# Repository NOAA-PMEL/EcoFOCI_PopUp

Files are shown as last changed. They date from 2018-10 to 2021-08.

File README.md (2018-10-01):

# EcoFOCI_PopUp

Under Ice 'Pop-Up' Buoy

################

Legal Disclaimer

This repository is a software product and is not official communication of the National Oceanic and Atmospheric Administration (NOAA), or the United States Department of Commerce (DOC). All NOAA GitHub project code is provided on an 'as is' basis and the user assumes responsibility for its use. Any claims against the DOC or DOC bureaus stemming from the use of this GitHub project will be governed by all applicable Federal law. Any reference to specific commercial products, processes, or services by service mark, trademark, manufacturer, or otherwise, does not constitute or imply their endorsement, recommendation, or favoring by the DOC. The DOC seal and logo, or the seal and logo of a DOC bureau, shall not be used in any manner to imply endorsement of any commercial product or activity by the DOC or the United States Government.

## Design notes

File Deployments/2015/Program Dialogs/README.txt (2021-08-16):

The 2015 prototypes did not have an arduino program to print a dialog or sampling schedule
They were proof of concept floats that had a wildlife computer attached
No program dialogs applicable for the prototype floats in 2015.
(S. Donohoe, 10/27/2020)

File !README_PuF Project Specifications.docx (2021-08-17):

Pop-up Project Specifications

(Low Cost Expendable Buoys for Under Ice Data Collection, Innovative Technology for Arctic Exploration (ITAE))

October 10, 2019

National Oceanic and Atmospheric Administration (NOAA)

Pacific Marine Environmental Lab (PMEL)

Ecosystem Fisheries-Oceanography Coordinated Investigations (EcoFOCI)

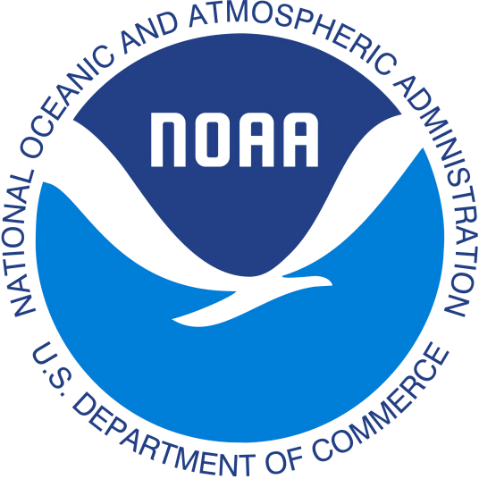
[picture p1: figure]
Image result for NOAA logo

# Revision History

The table below identifies all changes that have been incorporated into this document.

Version | Draft Date | Summary of Changes
1.0 | 10/10/2019 | Initial draft

# Table of Contents

Revision History 2

Table of Contents 3

INTRODUCTION 4

Purpose 4

Scope 4

IMMEDIATE SCIENCE APPLICATIONS 4

Under Ice Production 4

Measure conditions and productivity levels under sea ice. 4

Bering Cold Pool 4

Measure conditions in the Bering Sea to map the cold pool. 4

LONG-TERM PROJECT VISION 4

Measurements of Interest 5

Sampling Phases 6

ENGINEERING SPECIFICATIONS 6

Basic Program Flow 6

Mechanical Design Parameters 7

Sensor Capability/Data Quality 8

Battery Life/Data Quantity 10

APPENDIX A: ACRONYMS AND ABBREVIATIONS 10

APPENDIX B: CITATIONS 10

# INTRODUCTION

## Purpose

This document is to identify goals for the pop-up project that cover: overall project direction, specific engineering requirements, data quality and sensor capability requirements and cost requirements.

## Scope

This document is intended for use as a developmental tool while the pop-up project is under the auspices and funding of the ITAE program [1] (https://www.researchgate.net/publication/290392540_Innovative_technology_development_for_Arctic_Exploration). The pop-up project is a collaborative effort between EcoFOCI and the PMEL Engineering Development Division (EDD). Initial prototyping and development of the pop-up floats began under Lieutenant Daniel Langis, NOAA Corps in 2015 [2] (https://www.researchgate.net/publication/330300648_Low-Cost_Expendable_Buoys_for_Under_Ice_Data_Collection).

# IMMEDIATE SCIENCE APPLICATIONS

## Under Ice Production

### Measure conditions and productivity levels under sea ice.

  - The primary interest is in productivity at the water-ice boundary where productivity is very high in the spring before ice melt and ambient light levels are rapidly rising.

## Bering Cold Pool

### Measure conditions in the Bering Sea to map the cold pool.

  - Bottom temperatures below 2 °C characterize the Bering Sea cold pool, an important refuge for young pollock from predation. The primary interest is in measuring the extent, thickness and varying light levels of the cold pool through the winter months and how it changes over time.

# LONG-TERM PROJECT VISION

“Robust, inexpensive, and expendable, but sophisticated enough to acquire oceanographic-quality data.”

The pop-up float was developed as a unique product designed to fill the gap in available technology between year-round deeper moorings and surface-based sampling in the summers. However, because of the harsh and unpredictable environment of shifting and breaking ice, actually acquiring measurements close to the ice during the winter and spring without losing instruments has been notoriously difficult. The pop-up project aims to develop a low-cost, expendable oceanographic instrument that can be easily deployed by hand from any vessel and that will reliably transmit data back via satellite.

Long-term goals for this project include:

- maintaining low-cost production and deployment (~$3,000 / pop-up)
- an environmentally friendly design with biodegradable materials (glass, cork, metals)
- up to 24 month at-sea endurance
- the ability to send commands with 2-way communication to the float (commands to resend data files, change sampling frequencies...etc.)
- a modular design that allows sensors to be added or removed easily depending on mission and budget requirements.

## Measurements of Interest

Measurements of interest vary for the two current science applications: Bering Cold Pool and Under Ice Production. The Bering Cold Pool application focuses on temperature measurements with highest interest in further development to include a dissolved oxygen sensor. The Under Ice Production application focuses on Fluorescence and PAR, with interest in improving current camera capabilities.The following bulleted lists for each science application show the core instrument package for all floats in blue and additional sensors in order of priority.

    - GPS (only used during surface drifter mode)
    - Iridium SBD (only used during surface drifter mode)
    - Clock / Timer (RTC)
    - Profile (Primary) Temperature Probe (PTP)
    - Sea Surface (Secondary) Temperature (SST)
    - Pressure Sensor
    - Tilt
    - Fluorometer
    - Photosynthetically active radiation (PAR) (light months only)
    - Camera
    - Oxygen [currently cost-prohibitive]
    - Salinity [currently cost-prohibitive]

## Sampling Phases

The pop-up has a 5 phase sampling program: Anchored, Profile, Under Ice, Transmit and Surface Drifter. Each of these phases is run sequentially. Prior to the programmed unit start date, the pop-up is in sleep mode and is not sampling any sensors. The pop-up’s real time clock (RTC) functions as an alarm, which will wake up the unit and initiate the first sampling phase (Anchored) at the unit start date/time.

--ANCHORED--

This mode starts at the scheduled Start Time.

Unit will start sampling [Oct 01 2019 00:00:00] and take a sample every (1h,0m,0s)

--PROFILE--

This mode starts just before the scheduled Release Time.

Release Expected [Jun 01 2020 00:00:00] (<--Set Burn Wire Release for this exact time/date.)

Unit will wake up (2h,0m,0s) before scheduled release and wait for profile.

Start of profile will be triggered by a change in depth of (1 meters).

Profile will sample at 4 Hz for (0h,1m,30s) seconds before proceeding to phase 3.

If unit does not sense the release within (4h,0m,0s) of waking it will assume it missed the profile and proceed to the UNDER ICE phase.

--UNDER ICE --

This mode starts after profile has been collected (or missed).

Unit will take a sample every (1h,0m,0s) and take an image once a day.

Unit will search for GPS satellites for (0h,2m,0s) after every sample.

When unit acquires GPS fix, it will proceed to the TRANSMIT phase.

--TRANSMIT--

If unit does successfully find a GPS satellite, it will attempt to send all collected data back in the following order:

1-File Summary, 2-Profile Data, 3-Under Ice Data, 4-Bottom Data, 5-Daily Images

If any iridium messages send successfully, it will continue sending until one message fails and make the next attempt to send in (0h,20m,0s)

Otherwise, if no messages sent, the unit will take the next sample and attempt to send again in (1h,0m,0s)

--SURFACE DRIFTER--

This mode starts after all data has finished sending.

Unit will take a sample every (3h,0m,0s) and search for a GPS fix for (0h,2m,0s) after every sample.

Unit will attempt to send any new data regardless of whether a GPS fix was found

# ENGINEERING SPECIFICATIONS

## Basic Program Flow

A. Wake Up

B. Determine phase based on current date/time and programmed cutoff dates/times

0 = Initial programming (before start date)

If mode = 0, display parameters and shut down after user removes USB, don’t take any sample data

1 = Anchored

2 = Wait for Profile

3 = Under Ice

4 = Surface Drifter

C. Determine next sample time/date and set RTC alarm

D. Collect Sensor Data, Store to SD Card

E. If phase = 1 (Anchored)

Do nothing else, just go to sleep

F. If phase = 2 (Profile)

Take initial depth measurement

Continuously take depth readings and compare to initial measurement

Wait for depth to change by m meters

Start profile

Collect profile data at 4 Hz for p seconds

Go to sleep

G. If phase = 3 (Under Ice)

**This mode is used primarily to preserve battery power. In this mode the unit will only attempt to search for GPS once a day, rather than every hour.**

If hour = 23 UTC (1500 AKST, close to solar noon in most of Alaska)

Search for GPS for g seconds, n times, with delay in between

If GPS lock is found n times

Store GPS location and time on SD Card

Attempt to transmit iridium data

Else

Do nothing else, just go to sleep

H. If phase =4 (Surface Drifter)

Search for GPS for g seconds, n times, with delay in between

If GPS lock is found n times store GPS location and time on SD Card

Attempt to transmit iridium data

Else

Do nothing else, just go to sleep

## Mechanical Design Parameters

Trawl Housing Depth Rating: 200m, tested to max of 940psi (652m) at which point acrylic

camera housing cracked. Trawl float and delrin sensor housings withstood 940psi.

Buoyancy & GM:

The 12” trawl float provided ~28lb(?) net buoyancy. The net buoyancy should be tailored to produce the desired profile speed, while also providing adequate freeboard.

Profile speed: desired: ???? / actual: 1m/s

Freeboard: Generation 2 - 2.5” of freeboard

Generation 3 - 3.5” of freeboard

Generation 3.1 - 2.5” of freeboard

Total Dry Weight: Generation 2 - 13,305 g

Generation 3 - 11,263 g

Generation 3.1 - 13,305 g

Anchor Weight:

50lb Chain Link, 1m cable length

The anchor weight should be sufficient to keep the float from moving in high currents.

## Sensor Capability/Data Quality

Topside Temperature Probe (TTP) [Primary]*[3-4m resolution, ±0.01°C @4Hz]

Sensor: TTI inc, USP19572 REVA

Absolute Accuracy: ±0.01°C or better

Range: -5°C to +70°C

Resolution: 0.0006°C @ -2°C

0.001°C @ 10°C

0.002°C @25°C

0.01°C @50°C

Sea Surface Temperature (SST) [Secondary]*[3-4m resolution, ±0.01°C @4Hz]

Sensor: In-House (NTC Thermistor 50k Bead Epoxy,

Hex Head Plug 1/16”, Arctic Silver Alumina)

Absolute Accuracy: ±0.01°C or better

Range: -5°C to +70°C

Pressure Sensor *[ 3-4m resolution, ±1m @4Hz ]

Sensors: Keller PA-4LD OEM Pressure Transmitter (http://www.keller-druck.com/picts/pdf/engl/4ld_9ld_e.pdf)

Absolute Accuracy: ±70cm (10 bar) / ±0.7%FS

Range: 0 to 100m (10 bar) / 0 to 300m (30bar)

Resolution: 0.3cm (10 bar) /

GPS *[Position Accuracy ~3meters 50% CEP]

Unit: AMC-PA6H Alphamicro (http://www.alphamicrowireless.com/franchises/globaltop-technology/pa6h.aspx)

High Sensitivity: -165 dBm, TCXO Design

Position Accuracy: <3.0M 50% CEP

GPS Antenna: Adafruit External Active 960 (https://www.adafruit.com/product/960)

Iridium SBD *[full two-way communication system, DoD Network Whitelisted]

Unit: RockBLOCK 9603 (http://www.rock7mobile.com/products-rockblock-9603)

Power Consumption: max 450 mA (100mA required)

Iridium Antenna: Maxtena Helical 1621Mhz tuned patch antenna (https://www.maxtena.com/products/f-passive/m1621hct-ext/)

Clock

Unit: DS3234: RTC with Temperature Compensated Crystal Oscillator

Maximum Error: 1.05 minutes/year (0°C to 40°C)

1.84 minutes/year (-40°C to 85°C)

PAR *[±3%-5% @4Hz]

Sensor: Skye Instruments TAG-PARQ (Quantum) (https://www.skyeinstruments.com/applications/commercial-horticulture/light-sensors-systems-commercial-horticulture/par-quantum-sensors/)

Absolute Accuracy: ±3%-5% or better

Range: 0 to 1000 μmol/m²s

Sensitivity-current(I): 2μA/100μmol/m²s

Sensitivity-voltage(V): 1mV/100μmol/m²s

Response Time: 10ns

Tilt *[±2.0° @4Hz]

Sensor: ADXL345 3-Axis Digital Accelerometer

(http://www.analog.com/media/en/technical-documentation/data-sheets/ADXL345.pdf)Absolute Accuracy: Depends on Mounting/Calibration

Sensor is accurate for changes as little as 1.0°

Camera

Unit: μCAM-III (https://www.4dsystems.com.au/product/uCAM_III/)

Resolution: (80X60 / 160X120 / 160X128 / 640X480)

Output: Raw or JPEG

Lens Angle: 116 degrees

Fluorometer*[sample frequency @4Hz]

Sensor: Turner Designs Cyclops-7F (http://docs.turnerdesigns.com/t2/doc/brochures/S-0209.pdf)

Linear Range: 0-500μg/L

Minimum Detection: 0.03μg/L

Depth Range: 600m

Power Requirement: 240mW @ 12V

**Oxygen (https://www.mouser.com/SST-Sensing/Sensors/Environmental-Sensors/_/N-axfl1?P=1y8dmrj)*[±0.1% O2 saturation]

Sensor:

Oxygen range 0—25% O2

Oxygen pressure range 0—300mbar ppO2

Response time T90 < 10s (typical)

Accuracy

ppO2 < 2% FS

Temperature Indication only

Pressure ±5mbar

O2 Determined by ppO2 &

pressure accuracy

Resolution

ppO2 0.1mbar

Temperature 0.1°C

Pressure 1mbar

O2 0.01%

Lifetime > 5 years

**Salinity*[±0.1psu]

Sensor: Starr DST CTD (https://www.star-oddi.com/products/data-loggers/salinity-logger-probe-CTD)

*minimum requirement

**Currently cost or design prohibitive

## Battery Life/Data Quantity

Total Systems Battery Life: 24 month at-sea endurance

Primary Battery: 9V, 42Ah Alkaline Battery Pack (18 Standard D Cells)

RTC Battery: 3V 12.5mm Lithium Coin Cell (Energizer CR1220=40mAh)

GPS Backup Battery: 3V 12.5mm Lithium Coin Cell (Energizer CR1220=40mAh)

Burnwire Release Battery: 18V, 56Ah Alkaline Battery Pack (2 Standard 9V batteries)

Release Board Battery: 4.5V, 7.7Ah Alkaline Battery Pack (3 standard C Cells)

Data Storage: microSD or microSDHC card: 1GB to 32GB (FAT16 or FAT32)

Sample Limit: Limited by battery power and sample intervals

# APPENDIX A: ACRONYMS AND ABBREVIATIONS

NOAA National Oceanic & Atmospheric Administration

PMEL Pacific Marine Environmental Lab

EcoFOCI Ecosystem Fisheries-Oceanography Coordinated Investigations

EDD Engineering Development Division

ITAE Innovative Technology for Arctic Exploration

# APPENDIX B: CITATIONS

[1] (https://www.researchgate.net/publication/290392540_Innovative_technology_development_for_Arctic_Exploration) Cross, Jessica, C.W. Mordy, Heather Tabisola, Christian Meinig, E.D. Cokelet, and P.J.

Stabeno.“Innovative Technology Development for Arctic Exploration,” Vol. In publication,

2015. (https://doi.org/10.23919/OCEANS.2015.7404632)https://doi.org/10.23919/OCEANS.2015.7404632.

[2] (https://www.researchgate.net/publication/330300648_Low-Cost_Expendable_Buoys_for_Under_Ice_Data_Collection) Langis, D., P. Stabeno, Christian Meinig, C. Mordy, Shaun Bell, and Heather Tabisola. Low-Cost Expendable Buoys for Under Ice Data Collection, 2018. (https://doi.org/10.1109/OCEANS.2018.8604752)https://doi.org/10.1109/OCEANS.2018.8604752.

Pop-up Project Goals

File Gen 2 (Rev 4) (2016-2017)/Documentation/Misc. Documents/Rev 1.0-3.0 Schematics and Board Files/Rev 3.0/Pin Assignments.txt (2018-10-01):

#define TEMP_SWITCH 3
#define 5V_SENSOR_POWER 6
#define 3V3_SENSOR_POWER 8
#define GPS_ON 9
#define IRIDIUM_POWER 44
#define IRIDIUM_ON_OFF 47
#define ACCEL_CS A8
#define SDCARD_CS A5
#define RTC_CS A2
#define SHUTDOWN A0
#define GPS_TX 11
#define GPS_RX 12
#define IRIDIUM_RX A15
#define IRIDIUM_TX A14
#define SDA 20
#define SCL 21

pinMode(3,OUTPUT);
pinMode(6,OUTPUT);
pinMode(8,OUTPUT);
pinMode(9,OUTPUT);
pinMode(44,OUTPUT);
pinMode(47,OUTPUT);
pinMode(A8,OUTPUT);
pinMode(A5,OUTPUT);
pinMode(A2,OUTPUT);
pinMode(A0,OUTPUT);

digitalWrite(TEMP_SWITCH,LOW);
digitalWrite(5V_SENSOR_POWER,LOW);
digitalWrite(3V3_SENSOR_POWER,LOW);
digitalWrite(GPS_ON,LOW);
digitalWrite(IRIDIUM_POWER,LOW);
digitalWrite(IRIDIUM_ON_OFF,LOW);
digitalWrite(ACCEL_CS,HIGH);
digitalWrite(SDCARD_CS,HIGH);
digitalWrite(RTC_CS,HIGH);
digitalWrite(SHUTDOWN,HIGH);

SoftwareSerial ss(GPS_TX,GPS_RX);
SoftwareSerial nss(IRIDIUM_RX,IRIDIUM_TX);
Wire.begin();
IridiumSBD isbd(nss,IRIDIUM_ON_OFF);

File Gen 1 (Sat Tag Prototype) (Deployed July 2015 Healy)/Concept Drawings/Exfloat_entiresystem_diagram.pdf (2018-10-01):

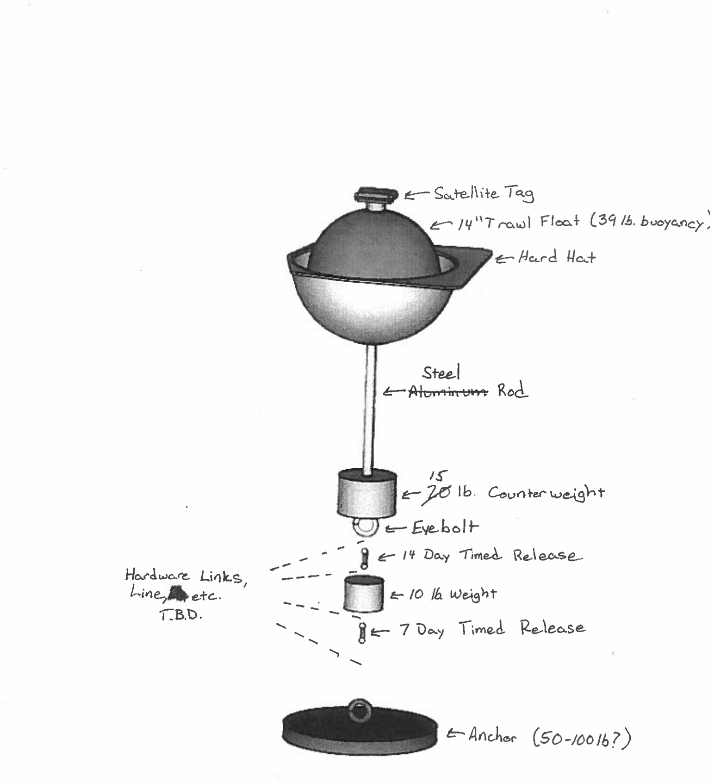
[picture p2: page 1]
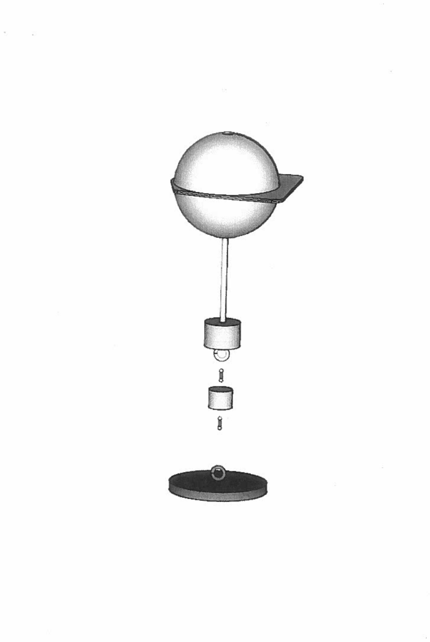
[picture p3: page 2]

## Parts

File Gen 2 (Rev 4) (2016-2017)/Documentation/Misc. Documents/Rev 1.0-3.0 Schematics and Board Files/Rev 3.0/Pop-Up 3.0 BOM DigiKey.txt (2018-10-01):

Identifier	Value	Part Number	Description	Qty	Size/Package	Size/Package	Comments	
"B1, B2"	"GPS Backup, RTC Backup"	952-1662-1-ND	Lithium Battery Clip	2	CR1220SMT	CR1220-SMD		
"B3, B4"	"GPS Coincell, RTC Coincell"	N033-ND	12mm 3V lithium coin cell	2	CR1220SMT	CR1220-SMD	DNP	
"C1,C3,C6,C7,C9,C10,C11,C12,C13,C14,C15,C16,C17,C22,C23,C24,C25,C27"	0.1 uF	399-5089-1-ND	Capacitor	18	CAP0603-CAP	0603-CAP		
"C2,C8"	4.7 uF	1276-2087-1-ND	Capacitor	2	CAP0603-CAP	0603-CAP		
C5	7.5pF	1276-2339-1-ND	Capacitor	1	CAP0603-CAP	0603-CAP		
C4	0.22 uF	445-1318-1-ND	Capacitor	1	CAP0603-CAP	0603-CAP		
"C18,C26"	10 uF	311-1376-1-ND	Capacitor	2	CAP1206-CAP	1206-CAP		
C19	3.3 uF	399-3694-1-ND	"Capacitor, Polarized Tantalum"	1	CAP1206-CAP	1206-CAP		
"C20,C21"	1 uF	311-1372-1-ND	Capacitor	2	CAP0603-CAP	0603-CAP		
D1	MBR0540	MBR0540TPMSCT-ND	"20V, 500mA"	1	SOD-123	SOD-123		
"D2, D3"	SM Sig	1N4148WSFSCT-ND	Diode	2	DIODESOD-323F	SOD-323F		
"JP1, JP4, JP6"	"PAR, Thermistor, BATT"	WM4800-ND	"0.100"" 2 Pin Male Header, Shrouded"	3	1x2 male header	1x02		
"J1, J4, J6"	"PAR Connector, Thermistor Connector, Batt Connector"	WM2900-ND	"0.100"" 2 Pin Female Housing, With Latch"	3	1x2 female housing	1x02	"Not on Board, DNP"	
"JP2, JP3"	"PRESSURE1, PRESSURE2"	WM4802-ND	"0.100"" 4 Pin Male Header, Shrouded"	2	1x5 male header	1X05		
"J2, J3"	"PRESSURE1 Connector, PRESSURE2 Connector"	WM2902-ND	"0.100"" 4 Pin Female Housing, With Latch"	2	1x5 female housing	1X05	"Not on Board, DNP"	
JP5	SMA_R/A	A97593-ND	"RF/COAXIAL, SMA JACK, R/A, 50OHM, THD"	1	901-143	AMPHENOL_901-143		
"Q1, Q2"	BSS138	BSS138CT-ND	N-Channel Mosfet	2	SOT23	SOT23		
"Q3,Q4,Q5,Q6"	AO3407A	785-1006-1-ND	P-Channel Mosfet	4	SOT23	SOT23		
R1	"33.2k, 1%"	311-33.2KHRCT-ND	Resistor	1	R-US_R0603	R0603		
R2	"1.15k, 1%"	311-1.15KHRCT-ND	Resistor	1	R-US_R0603	R0603		
R3	"200k, 0.1%"	P200KDBCT-ND	Resistor	1	R-US_R0603	R0603		
R4	"33K, 1%"	311-33KGRCT-ND	Resistor	1	R-US_R0603	R0603		
R6	"49.9K, 1%"	311-49.9KHRCT-ND	Resistor	1	R-US_R0603	R0603		
"R5,R7,R9,R11"	"3.74k, 1%"	311-3.74KHRCT-ND	Resistor	4	R-US_R0603	R0603		
R12	10k**	Y1630-10.0KBCT-ND	"Resistor, 0.01%, 0.2PPM"	1	R-US_R1206	R1206		
"R17,R18,R21,R23,R25,R27"	1k	311-1.0KGRCT-ND	Resistor	6	R-US_R0603	R0603		
"R19,R20,R22,R24"	100k	311-100KGRCT-ND	Resistor	4	R-US_R0603	R0603		
"R26,R28"	10k	311-10KGRCT-ND	Resistor	2	R-US_R0603	R0603		
TR1	10k	615-1069-ND	Thermistor	1	"THERMISTOR-2,5"	"RS-2,5"	"Not on Board, DNP"	
"SHTDN, ALARM,  MOSI3v3, MISO3v3, SCK3v3, MOSI5v, MISO5v, SCK5v, SDA3V3, SCL3V3, SDA5V, SCL5V, GPSRX3V3, GPSTX3V3, GPSRX5V, GPSTX5V, VPAR"	TP-040	36-5004-ND	"Test Point, Yellow"	18	TP-040	TP-040		
"GND1,GND2,GND3"	TP-040	36-5001-ND	"Test Point, Black"	3	TP-040	TP-040		
"VBATT,+5V,+3V3, +3VP**,+3VT**"	TP-040	36-5000-ND	"Test Point, Red"	4	TP-040	TP-040		
"U1,U4"	MAX6126	MAX6126AASA30+-ND	"3V, 0.02% Precision Voltage Regulator"	2	MAX6126	SOIC127P600X175-8N		
U2	ADS1100-A1	296-14298-1-ND	Self-Calibrating 16 Bit ADC - Address A1	1	ADS1100A0IDBVT	SOT95P280X145-6N		
U3	OPA320	296-29510-1-ND	Operational Amplifier	1	OPA320AIDBVT	SOT95P280X145-5N		
"U8,U14"	M74VHC1GT125	M74VHC1GT125DF1GOSCT-ND	Noninverting Buffer / CMOS Logic Level Shifter	2	M74VHC1GT125DF1G	SOT65P210X110-5N		
U6	ADS1100-A0	296-12966-1-ND	Self-Calibrating 16 Bit ADC - Address A0	1	ADS1100A0IDBVT	SOT95P280X145-6N		
U7	ADG836	ADG836LYRMZ-ND	SPDT Switch	1	ADG836	MSOP10		
U9	FGPMMOPA6H	https://www.adafruit.com/products/790	GPS Module - MTK MT3339 Chipset	1	GPS_FGPMMOPA6H	FGPMMOPA6H		
"U5, U11"	NL17SZ07DFT2G	NL17SZ07DFT2GOSCT-ND	Single Non-Inverting Buffer 	2	NL17SZ07DFT2G	SOT65P210X110-5N		
U10	SN74LVC1G32DCKR	296-9848-1-ND	Single OR Gate	1	SC-70-5	SC-70-5		
U12	Arduino Mega 2650		Arduino Mega 2650	1	Arduino Mega 2650	Arduino Mega 2650	"**Populate with 0.100"" headers, HF… and HM…"	
U13	RockBlock Mk2		RockBlock Mk2	1	RockBlock Mk2	RockBlock Mk2	"**Populate with 0.100"" headers, HF… and HM…"	
U15	M74HC4050	296-14529-1-ND	HEX BUFFER/CONVERTER	1	M74HC4050RM13TR	SOIC127P600X175-16N		
U16	SDCard Socket	101-00660-68-6-1-ND	microSD Socket	1	USD-SOCKETNEW	MICRO-SD-SOCKET-PP		
U17	ADXL345	ADXL345BCCZ-ND	"3-Axis, Digital Accelerometer"	1	ADXL345	LGA14		
U18	LP5907	296-38557-1-ND	50-mA LOW-DROPOUT LINEAR REGULATOR	1	TPS77033	SOT23-DBV		
U19	Inverter	NC7S14M5XCT-ND	SINGLE SCHMITT-TRIGGER INVERTER	1	1P1G14MDBVREPG4	SOT95P280X145-5N		
U20	DS3234	DS3234SN#T&RCT-ND	SPI RTC module 	1	DS3234	DS3234		
U21	LT1129	LT1129IQ-5#PBF-ND	5V Voltage Regulator	1	LT1129CQ-5	Q5-DD		
U22	LT1013	296-12982-1-ND	1 MHz Op Amp	1	8-SOIC	8-SOIC		
U22	LT1634	LT1634BIS8-1.25#PBF-ND	1.25V Shunt Regulator	1	8-SOIC	8-SOIC		LT1634AIS8-1.25#PBF-ND
HF1	1x6	S7039-ND	"1x6 female header, unshrouded"	1	1x6 female header	1x6 	"**not labeled on board, see photo"	
HF2	1x8	S7041-ND	"1x8 female header, unshrouded"	1	1x8 female header	1x8	"**not labeled on board, see photo"	
HF3	2x3	S7106-ND	"2x3 female header, unshrouded"	1	2x3 female header	2x3	"**not labeled on board, see photo"	
"HM1,HM2,HM3,HM4,HM5,HM6,HM7"	1x8	952-2271-ND	"1x8 male header, unshrouded"	7	1x8 male header	1x8	"**not labeled on board, see photo"	
"HM8,HM9,HM10"	1x10	952-1843-ND	"1x10 male header, unshrouded"	3	1x10 male header	1x10	"**not labeled on board, see photo"

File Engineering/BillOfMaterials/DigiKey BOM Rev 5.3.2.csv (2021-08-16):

Identifier | Value | Part Number | Description | Qty
B1, B2 | GPS Backup, RTC Backup | 952-1662-1-ND | Lithium Battery Clip | 2
C1 | 11pF | 399-8787-1-ND | Capacitor | 1
C2,C3,C5,C6,C7,C9,C10,C11,C12,C13,C14,C15,C16,C17,C22,C23,C24,C25,C27,C28,C29 | 0.1 uF | 399-5089-1-ND | Capacitor | 21
C4,C8 | 4.7 uF | 587-3416-1-ND | Capacitor | 2
C18,C26 | 10 uF | 311-1376-1-ND | Capacitor | 2
C19 | 3.3 uF | 399-10443-1-ND | Capacitor, Polarized Tantalum | 1
C20,C21 | 1 uF | 587-3413-1-ND | Capacitor | 2
D1 | MBR0540 | MBR0540TPMSCT-ND | 20V, 500mA | 1
D2, D3 | BAT46JFILM | 497-6653-1-ND | DIODE SCHOTTKY 100V 150MA SOD323 | 2
JP1, JP3, JP4, JP6 | PAR Connector, SST Connector, Thermistor Connector, Batt Connector | WM10658-ND | 1x2 Micro-fit 3.0 Header | 4
JP2 | PRESSURE Connector | WM10669-ND | 1x4 Micro-fit 3.0 Header | 1
JP5 | SMA | A97594-ND | CONN SMA JACK STR 50 OHM PCB | 1
JP7 | FLUOR | WM10679-ND | 2x3 Micro-fit 3.0 Header | 1
JP8 | RockBlock9603 | WM7614CT-ND | 1x10 PicoBlade Header | 1
JP9 | UCAM-III | WM1920-ND | 1x5 Micro-fit 3.0 Header | 2
Q1, Q2 | BSS138 | BSS138-FDICT-ND | N-Channel Mosfet | 2
Q3,Q4,Q5,Q6,Q7,Q8 | AO3407A | 785-1006-1-ND | P-Channel Mosfet | 6
R1 | 137k, 0.1% | P137KDBDKR-ND | Resistor | 1
R2 | 10k, 0.1% | P10KDBCT-ND | Resistor | 1
R3 | 2k, 0.1% | P2.0KDBCT-ND | Resistor | 1
R4 | 200K, 1% | 311-200KFRCT-ND | Resistor | 1
R5,R7,R9,R11 | 3.74k, 1% | RMCF0603FT3K74CT-ND | Resistor | 4
R6 | 324K, 0.1% | P324KBCCT-ND | Resistor | 1
R8,R10,R26,R28 | 10k | MCT0603-10.0K-CFCT-ND | Resistor | 4
R12 | 50k,0.01% | Y1627-50KCT-ND | Resistor, 0.01%, 0.2PPM | 1
R13,R14,R15,R17,R18,R21,R23,R25,R27,R30,R32 | 1k | P1.00KHCT-ND | Resistor | 11
R16,R19,R20,R22,R24,R31 | 100k | P100KHCT-ND | Resistor | 6
R29 | 6.98k, 1% | 541-6.98HHCT-ND | Resistor | 1
SHTDN, ALARM, MOSI3v3, MISO3v3, SCK3v3, MOSI5v, MISO5v, SCK5v, SDA3V3, SCL3V3, SDA5V, SCL5V, VPAR | TP-040 | 36-5004-ND | Test Point, Yellow | 13
GND1,GND2,GND3 | TP-040 | 36-5001-ND | Test Point, Black | 3
VBATT,+5V,+3V3, +3VP*,+3VT* | TP-040 | 36-5000-ND | Test Point, Red | 5
U1,U4 | MAX6126 | MAX6126AASA30+-ND | 3V, 0.02% Precision Voltage Regulator | 2
U2 | ADS1100-A1 | 296-14298-1-ND | Self-Calibrating 16 Bit ADC - Address A1 | 1
U3 | OPA320 | 296-29510-1-ND | Operational Amplifier | 1
U6 | ADS1100-A0 | 296-12966-1-ND | Self-Calibrating 16 Bit ADC - Address A0 | 1
U7 | ADG836 | ADG836LYRMZ-ND | SPDT Switch | 1
U5,U8 | NL17SZ07DFT2G | NL17SZ07DFT2GOSCT-ND | Single Non-Inverting Buffer | 2
U9 | FGPMMOPA6H | https://www.adafruit.com/products/790 | GPS Module - MTK MT3339 Chipset | 1
U10 | SN74LVC1G32DCKR | 296-9848-1-ND | Single OR Gate | 1
U11 | MAX4624EUT | MAX4624EUT+TCT-ND | IC SWITCH SPDT SOT23-6 | 1
U14 | M74VHC1GT125 | M74VHC1GT125DF1GOSCT-ND | Noninverting Buffer / CMOS Logic Level Shifter | 1
U15 | M74HC4050 | 296-14529-1-ND | HEX BUFFER/CONVERTER | 1
U16 | SDCard Socket | 3M5607CT-ND | microSD Socket | 1
U17 | ADXL345 | ADXL345BCCZ-ND | 3-Axis, Digital Accelerometer | 1
U18 | LP5907 | 296-38557-1-ND | 250-mA LOW-DROPOUT LINEAR REGULATOR | 1
U19 | Inverter | NC7S14M5XCT-ND | SINGLE SCHMITT-TRIGGER INVERTER | 1
U20 | DS3234 | DS3234SN#T&RCT-ND | SPI RTC module | 1
U21 | LT1129 | LT1129IQ-5#PBF-ND | 5V Voltage Regulator | 1
U22 | LT1013 | 296-12982-1-ND | 1 MHz Op Amp | 1
U23 | LT1634 | LT1634BIS8-1.25#PBF-ND | 1.25V Shunt Regulator | 1
U24 | ADS1100-A2 | 296-14299-1-ND | Self-Calibrating 16 Bit ADC - Address A2 | 1
U25 | TS5A21366DCUR | 296-24304-1-ND | IC SWITCH DUAL SPST US8 | 1
U26 | TXB0106PWR | 296-23759-1-ND | IC 6BIT NON-INV TRANSLTR 16TSSOP | 1
HF3 | 2x3 | S7106-ND | 2x3 female header, unshrouded | 1
HM1,HM2,HM3,HM4,HM5,HM6,HM7 | 1x8 | 952-2271-ND | 1x8 male header, unshrouded | 7
HM8,HM9,HM10 | 1x10 | 952-1843-ND | 1x10 male header, unshrouded | 3

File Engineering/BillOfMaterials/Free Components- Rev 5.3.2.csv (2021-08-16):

Identifier | Value | Part Number | Description | Qty per Float
B3, B4 | GPS Coincell, RTC Coincell | N033-ND | 12mm 3V lithium coin cell | 2
J1, J3, J4, J6 | PAR, SST, TEMP, BATT | WM1845-ND | 1x2 Micro-fit 3.0 Conn | 4
J2 | PRESSURE | WM1847-ND | 1x4 Micro-fit 3.0 Conn | 1
J7 | FLUOR | WM1785-ND | 2x3 Micro-fit 3.0 Conn | 1
J8 | RockBlock9603 | WM17199-ND | 1x10 PicoBlade Cable Assembly | 1
J9 | UCAM-III | WM1848-ND | 1x5 Micro-fit 3.0 Conn | 1
X1 | MicroPin | WM1839-ND | Microfit Pin (20-24 AWG) | 25
X2 | MicroPin | WM1840-ND | Microfit Pin (26-30 AWG) | 25

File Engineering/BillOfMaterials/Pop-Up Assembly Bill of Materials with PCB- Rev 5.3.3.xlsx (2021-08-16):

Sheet: Sensors and Comms
Assembly Variant | Item Description | Purpose | Vendor | Product Number | Link | Cost | Qty Per Pack | Qty Per Float | Select? (y/n) | Cost Per Float | Qty On-Hand | Comments | Exchange Rate
All | TAG-PARQ Sensor | PAR Sensor | Skye Instruments | TAG-PARQ | katie@skyeinstruments.com, adam@skyeinstruments.com | £270.00 | 1 | 1 | n | $0.00 | 10 | Exchange Rate 1GBP= __ USD --->>> | 1.35
All | 10 bar Pressure Sensor | Pressure Sensor | Keller | PA4LD/81974.30/10Bar | http://www.keller-druck.com/home_e/paprod_e/4ld_e.asp | $117.75 | 1 | 1 | y | $117.75 | 26
All | Endcap Temperature Probe | Temperature Probe | (TTI) | USP19572 REV A | http://www.ussensor.com/h2081-npt-stainless-steel | $67.00 | 1 | 1 | y | $67.00 | 30
 | SST thermistor | 50KOhm NTC Thermistor | Digikey | 615-1071-ND | https://www.digikey.com/products/en?keywords=615-1071-ND | $165.00 | 25 | 1 | y | $6.60 | 23
 | SST housing | 1/16" Hex Head Plug | Grainger | 20YZ95 | https://www.grainger.com/product/20YZ95?RIID=50923575175&GID=725084957&mid=EMT-_-10376092-_-ShipConfirmation-_-Item | $7.72 | 1 | 1 | y | $7.72 | 23
All | SST thermal adhesive | Thermal Adhesive | Arctic Silver | Silver or Alumina | https://www.amazon.com/Arctic-Silver-Premium-Adhesive-ASTA-7G/dp/B0087X7262?hvadid=177262826597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 | $23.79 | 1 | 0.15 | y | $3.57 | 6
All | u-CAM-III | Camera | Digikey | UCAM-III | https://www.digikey.com/product-detail/en/4d-systems-pty-ltd/UCAM-III/1613-1369-ND/6623663 | $49.98 | 1 | 1 | n | $0.00 | 7
All | u-CAM-III 116° Lens | Camera Lens | Digikey | UCAM-III-116LENS | https://www.digikey.com/product-detail/en/4d-systems-pty-ltd/UCAM-III-116LENS/1613-1079-ND/5725467 | $10.19 | 1 | 1 | n | $0.00 | 7
All | Tilt Sensor | Tilt Sensor | N/A | N/A | N/A | N/A | N/A | N/A | N/A | N/A |  | Tilt sensor (accelerometer) is integrated in main PCB
All | RockBLOCK Mk3 | Iridium Module | RockSeven | RockBLOCK 9603 | https://www.rock7.com/shop-product-detail?productId=51 | $249.00 | 1 | 1 | y | $249.00 | 21 | Also Available Directly from Manufacturer - https://www.rock7mobile.com/shop
All | RockBLOCK Mk3 Iridium Whitelisting | Whitelist Iridium for DITCO Network | NAL Research Corporation | RockBLOCK 9603 | Angela Roush <ARoush@nalresearch.com> | $35.00 | 1 | 1 | y | $35.00 | 21
All | RockBLOCK Mk3 Iridium Unlock Fee | Unlock Iridium for DITCO Network | RockSeven | RockBLOCK 9603 | info@rock7.com | $60.00 | 1 | 1 | y | $60.00
All | Maxtena Helical Antenna | Iridium Antenna | Newark | M1621HCT-EXT | http://www.newark.com/maxtena/m1621hct-ext/antenna-iridium-1-616-1-626ghz/dp/52Y3292?CMP=AFC-OP | $53.74 | 1 | 1 | y | $53.74 | 21 | Also Available from Rock Seven- https://www.rock7mobile.com/shop
All | Ladybird 1 GPS - MT3339 ChipSet | GPS Module | Alphamicro | AMC-PA6H | http://www.alphamicrowireless.com/franchises/globaltop-technology/pa6h.aspx | $22.50 | 1 | 1 | y | $22.50 | 22 | Contact - sue.sampson@alphamicro.net. Also available at https://www.adafruit.com/products/790
All | GPS Active External Antenna | GPS Antenna | Adafruit | N/A | https://www.adafruit.com/products/960 | $12.95 | 1 | 1 | y | $12.95 | 21
With Fluorometer | Turner Cyclops 7 Fluorometer (No Housing) | Fluorometer | Turner Designs | 2110-000-C-NH | http://www.turnerdesigns.com/products/submersible-fluorometer/cyclops-7f-submersible-fluorescence-and-turbidity-sensors?page=shop.product_details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 | $1475.00 | 1 | 1 | n | $0.00 | 0
 |  |  |  |  |  |  |  |  |  | $635.83 |  | TOTAL
 |  |  |  |  |  |  |  |  |  |  |  | 1

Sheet: Battery
Assembly Variant | Item Description | Purpose | Vendor | Product Number | Link | Cost | Qty Per Pack | Qty Per Float | Cost Per Float | Qty On-Hand | Comments
All | 9V, 42Ah, 18 D-Cell Alkaline Battery | Primary Battery | Apak Batteries | AP0015 | apakbatteries@gmail.com | $92.54 | 1 | 1 | $92.54 | 20
All | 18V, 56Ah, 2 9V Alkaline Battery | Pop-up Release Burn | Apak Batteries | AP002 | apakbatteries@gmail.com | $14.67 | 1 | 1 | $14.67 | 5
All | 4.5V, 7.7Ah, 3 C-Cell Alkaline Battery | Pop-up Release Board | Apak Batteries | AP0035 | apakbatteries@gmail.com | $13.56 | 1 | 1 | $13.56 | 4 | 10 w/ dbl(14 Ah) On Hand
All | Gap-Sealing Spray Foam Insulation Can | Spray Foam for Battery | McMaster | 8551K11 | https://www.mcmaster.com/#8551k11/=169p3e9 | $8.66 | 1 | 0.5 | $4.33 | 6 | Each Can is enough for 2-3 Floats
All | Thick-Wall PVC Pipe Fitting for Water, Flanged 1-1/4 Pipe Size Socket-Connect Adapter | Battery Mount for Bottom of Float | McMaster | 4881K215 | https://www.mcmaster.com/#4881k215/=1czvwsl | $8.03 | 1 | 1 | $8.03 | 20
 |  |  |  |  |  |  |  |  | $133.13 |  | TOTAL

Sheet: Printed Circuit Board
Identifier | Value | Part Number | Description | Qty per board | Comments
B1, B2 | GPS Backup, RTC Backup | 952-1662-1-ND | Lithium Battery Clip | 2 | Place Blob of Solder on center Pad
B3, B4 | GPS Coincell, RTC Coincell | N033-ND | 12mm 3V lithium coin cell | 2 | DNP
C1 | 11pF | 399-8787-1-ND | Capacitor | 1
C2,C3,C5,C6,C7,C9,C10,C11,C12,C13,C14,C15,C16,C17,C22,C23,C24,C25,C27,C28,C29 | 0.1 uF | 311-1344-1-ND (https://www.digikey.com/product-detail/en/yageo/CC0603KRX7R9BB104/311-1344-1-ND/2103128) | Capacitor | 21
C4,C8 | 4.7 uF | 587-3416-1-ND | Capacitor | 2
C18,C26 | 10 uF | 311-1376-1-ND | Capacitor | 2
C19 | 3.3 uF | 399-10443-1-ND | Capacitor, Polarized Tantalum | 1
C20,C21 | 1 uF | 587-1242-1-ND (https://www.digikey.com/product-detail/en/taiyo-yuden/LMK107B7105KA-T/587-1242-1-ND/931019) | Capacitor | 2
D1 | MBR0540 | MBR0540TPMSCT-ND | 20V, 500mA | 1
D2, D3 | BAT46JFILM | 497-6653-1-ND | DIODE SCHOTTKY 100V 150MA SOD323 | 2
J1, J3, J4, J6 | PAR, SST, TEMP, BATT | WM1845-ND | 1x2 Micro-fit 3.0 Conn | 4 | Not on Board, DNP
JP1, JP3, JP4, JP6 | PAR Connector, SST Connector, Thermistor Connector, Batt Connector | WM10658-ND | 1x2 Micro-fit 3.0 Header | 4
J2 | PRESSURE | WM1847-ND | 1x4 Micro-fit 3.0 Conn | 1 | Not on Board, DNP
JP2 | PRESSURE Connector | WM10669-ND | 1x4 Micro-fit 3.0 Header | 1
JP5 | SMA | A97594-ND | CONN SMA JACK STR 50 OHM PCB | 1
J7 | FLUOR | WM1785-ND | 2x3 Micro-fit 3.0 Conn | 1 | Not on Board, DNP
JP7 | FLUOR | WM10679-ND | 2x3 Micro-fit 3.0 Header | 1
J8 | RockBlock9603 | WM17199-ND | 1x10 PicoBlade Cable Assembly | 1 | Not on Board, DNP
JP8 | RockBlock9603 | WM7614CT-ND | 1x10 PicoBlade Header | 1
J9 | UCAM-III | WM1848-ND | 1x5 Micro-fit 3.0 Conn | 1 | Not on Board, DNP
JP9 | UCAM-III | WM1920-ND | 1x5 Micro-fit 3.0 Header | 2 | 1 Not On Board
X1 | MicroPin | WM1839-ND | Microfit Pin (20-24 AWG) | 25 | Not on Board, DNP
X2 | MicroPin | WM1840-ND | Microfit Pin (26-30 AWG) | 25 | Not on Board, DNP
Q1, Q2 | BSS138Q-7-F | BSS138Q-7-FDICT-ND (https://www.digikey.com/product-detail/en/diodes-incorporated/BSS138Q-7-F/BSS138Q-7-FDICT-ND/8283864) | N-Channel Mosfet | 2
Q3,Q4,Q5,Q6,Q7,Q8 | AO3407A | 785-1006-1-ND | P-Channel Mosfet | 6
R1 | 137k, 0.1% | P137KDBDKR-ND | Resistor | 1
R2 | 10k, 0.1% | P10KDBCT-ND | Resistor | 1
R3 | 2k, 0.1% | P2.0KDBCT-ND | Resistor | 1
R4 | 200K, 1% | 311-200KFRCT-ND | Resistor | 1
R5,R7,R9,R11 | 3.74k, 1% | RMCF0603FT3K74CT-ND | Resistor | 4
R6 | 324K, 0.1% | P324KBCCT-ND | Resistor | 1
R8,R10,R26,R28 | 10k | MCT0603-10.0K-CFCT-ND | Resistor | 4
R12 | 50k,0.01% | Y1627-50KCT-ND | Resistor, 0.01%, 0.2PPM | 1
R13,R14,R15,R17,R18,R21,R23,R25,R27,R30,R32 | 1k | P1.00KHCT-ND | Resistor | 11
R16,R19,R20,R22,R24,R31 | 100k | P100KHCT-ND | Resistor | 6
R29 | 6.98k, 1% | RMCF0603FT6R98CT-ND (https://www.digikey.com/product-detail/en/stackpole-electronics-inc/RMCF0603FT6R98/RMCF0603FT6R98CT-ND/7790076) | Resistor | 1
SHTDN, ALARM, MOSI3v3, MISO3v3, SCK3v3, MOSI5v, MISO5v, SCK5v, SDA3V3, SCL3V3, SDA5V, SCL5V, VPAR | TP-040 | 36-5004-ND | Test Point, Yellow | 13
GND1,GND2,GND3 | TP-040 | 36-5001-ND | Test Point, Black | 3
VBATT,+5V,+3V3, +3VP*,+3VT* | TP-040 | 36-5000-ND | Test Point, Red | 5
U1,U4 | MAX6126 | MAX6126AASA30+-ND | 3V, 0.02% Precision Voltage Regulator | 2
U2 | ADS1100-A1 | 296-14298-1-ND | Self-Calibrating 16 Bit ADC - Address A1 | 1
U3 | OPA320 | 296-29510-1-ND | Operational Amplifier | 1
U6 | ADS1100-A0 | 296-12966-1-ND | Self-Calibrating 16 Bit ADC - Address A0 | 1
U7 | ADG836 | ADG836YRMZ-ND (https://www.digikey.com/product-detail/en/analog-devices-inc/ADG836YRMZ/ADG836YRMZ-ND/820127) | SPDT Switch | 1
U5,U8 | NL17SZ07DFT2G | NL17SZ07DFT2GOSCT-ND | Single Non-Inverting Buffer | 2
U9 | FGPMMOPA6H | https://www.adafruit.com/products/790 | GPS Module - MTK MT3339 Chipset | 1
U10 | SN74LVC1G32DCKR | 296-9848-1-ND | Single OR Gate | 1
U11 | MAX4624EUT | MAX4624EUT+TCT-ND | IC SWITCH SPDT SOT23-6 | 1
U12 | Arduino Mega 2650 | 1050-1018-ND | Arduino Mega 2650 | 1 | DNP
U13 | RockBlock9603 |  | RockBlock9603 | 1 | DNP
U14 | M74VHC1GT125 | M74VHC1GT125DF1GOSCT-ND | Noninverting Buffer / CMOS Logic Level Shifter | 1
U15 | M74HC4050 | 296-14529-1-ND | HEX BUFFER/CONVERTER | 1
U16 | SDCard Socket | 3M5607CT-ND | microSD Socket | 1
U17 | ADXL345 | ADXL345BCCZ-ND | 3-Axis, Digital Accelerometer | 1
U18 | LP5907 | 296-38557-1-ND | 250-mA LOW-DROPOUT LINEAR REGULATOR | 1
U19 | Inverter | NC7S14M5XCT-ND | SINGLE SCHMITT-TRIGGER INVERTER | 1
U20 | DS3234 | DS3234SN#T&RCT-ND | SPI RTC module | 1
U21 | LT1129 | LT1129IQ-5#PBF-ND | 5V Voltage Regulator | 1
U22 | LT1013 | 296-12982-1-ND | 1 MHz Op Amp | 1
U23 | LT1634 | LT1634BIS8-1.25#PBF-ND | 1.25V Shunt Regulator | 1
U24 | ADS1100-A2 | 296-14299-1-ND | Self-Calibrating 16 Bit ADC - Address A2 | 1
U25 | TS5A21366DCUR | 296-24304-1-ND | IC SWITCH DUAL SPST US8 | 1
U26 | TXB0106PWR | 296-23759-1-ND | IC 6BIT NON-INV TRANSLTR 16TSSOP | 1
HF3 | 2x3 | S7106-ND | 2x3 female header, unshrouded | 1 | **not labeled on board, see photo
HM1,HM2,HM3,HM4,HM5,HM6,HM7 | 1x8 | 952-2271-ND | 1x8 male header, unshrouded | 7 | **not labeled on board, see photo
HM8,HM9,HM10 | 1x10 | 952-1843-ND | 1x10 male header, unshrouded | 3 | **not labeled on board, see photo

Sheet: PCB Assembly BOM
Identifier | Value | Part Number | Description | Qty per board | Comments
B1, B2 | GPS Backup, RTC Backup | 952-1662-1-ND | Lithium Battery Clip | 2 | Place Blob of Solder on center Pad
C1 | 11pF | 399-8787-1-ND | Capacitor | 1
C2,C3,C5,C6,C7,C9,C10,C11,C12,C13,C14,C15,C16,C17,C22,C23,C24,C25,C27,C28,C29 | 0.1 uF | 311-1344-1-ND (https://www.digikey.com/product-detail/en/yageo/CC0603KRX7R9BB104/311-1344-1-ND/2103128) | Capacitor | 21
C4,C8 | 4.7 uF | 587-3416-1-ND | Capacitor | 2
C18,C26 | 10 uF | 311-1376-1-ND | Capacitor | 2
C19 | 3.3 uF | 399-10443-1-ND | Capacitor, Polarized Tantalum | 1
C20,C21 | 1 uF | 587-1242-1-ND (https://www.digikey.com/product-detail/en/taiyo-yuden/LMK107B7105KA-T/587-1242-1-ND/931019) | Capacitor | 2
D1 | MBR0540 | MBR0540TPMSCT-ND | 20V, 500mA | 1
D2, D3 | BAT46JFILM | 497-6653-1-ND | DIODE SCHOTTKY 100V 150MA SOD323 | 2
JP1, JP3, JP4, JP6 | PAR Connector, SST Connector, Thermistor Connector, Batt Connector | WM10658-ND | 1x2 Micro-fit 3.0 Header | 4
JP2 | PRESSURE Connector | WM10669-ND | 1x4 Micro-fit 3.0 Header | 1
JP5 | SMA | A97594-ND | CONN SMA JACK STR 50 OHM PCB | 1
JP7 | FLUOR | WM10679-ND | 2x3 Micro-fit 3.0 Header | 1
JP8 | RockBlock9603 | WM7614CT-ND | 1x10 PicoBlade Header | 1
JP9 | UCAM-III | WM1920-ND | 1x5 Micro-fit 3.0 Header | 2 | 1 Not On Board
Q1, Q2 | BSS138Q-7-F | BSS138Q-7-FDICT-ND (https://www.digikey.com/product-detail/en/diodes-incorporated/BSS138Q-7-F/BSS138Q-7-FDICT-ND/8283864) | N-Channel Mosfet | 2
Q3,Q4,Q5,Q6,Q7,Q8 | AO3407A | 785-1006-1-ND | P-Channel Mosfet | 6
R1 | 137k, 0.1% | P137KDBDKR-ND | Resistor | 1
R2 | 10k, 0.1% | P10KDBCT-ND | Resistor | 1
R3 | 2k, 0.1% | P2.0KDBCT-ND | Resistor | 1
R4 | 200K, 1% | 311-200KFRCT-ND | Resistor | 1
R5,R7,R9,R11 | 3.74k, 1% | RMCF0603FT3K74CT-ND | Resistor | 4
R6 | 324K, 0.1% | P324KBCCT-ND | Resistor | 1
R8,R10,R26,R28 | 10k | MCT0603-10.0K-CFCT-ND | Resistor | 4
R12 | 50k,0.01% | Y1627-50KCT-ND | Resistor, 0.01%, 0.2PPM | 1
R13,R14,R15,R17,R18,R21,R23,R25,R27,R30,R32 | 1k | P1.00KHCT-ND | Resistor | 11
R16,R19,R20,R22,R24,R31 | 100k | P100KHCT-ND | Resistor | 6
R29 | 6.98k, 1% | RMCF0603FT6R98CT-ND (https://www.digikey.com/product-detail/en/stackpole-electronics-inc/RMCF0603FT6R98/RMCF0603FT6R98CT-ND/7790076) | Resistor | 1
SHTDN, ALARM, MOSI3v3, MISO3v3, SCK3v3, MOSI5v, MISO5v, SCK5v, SDA3V3, SCL3V3, SDA5V, SCL5V, VPAR | TP-040 | 36-5004-ND | Test Point, Yellow | 13
GND1,GND2,GND3 | TP-040 | 36-5001-ND | Test Point, Black | 3
VBATT,+5V,+3V3, +3VP*,+3VT* | TP-040 | 36-5000-ND | Test Point, Red | 5
U1,U4 | MAX6126 | MAX6126AASA30+-ND | 3V, 0.02% Precision Voltage Regulator | 2
U2 | ADS1100-A1 | 296-14298-1-ND | Self-Calibrating 16 Bit ADC - Address A1 | 1
U3 | OPA320 | 296-29510-1-ND | Operational Amplifier | 1
U6 | ADS1100-A0 | 296-12966-1-ND | Self-Calibrating 16 Bit ADC - Address A0 | 1
U7 | ADG836 | ADG836YRMZ-ND (https://www.digikey.com/product-detail/en/analog-devices-inc/ADG836YRMZ/ADG836YRMZ-ND/820127) | SPDT Switch | 1
U5,U8 | NL17SZ07DFT2G | NL17SZ07DFT2GOSCT-ND | Single Non-Inverting Buffer | 2
U9 | FGPMMOPA6H | https://www.adafruit.com/products/790 | GPS Module - MTK MT3339 Chipset | 1
U10 | SN74LVC1G32DCKR | 296-9848-1-ND | Single OR Gate | 1
U11 | MAX4624EUT | MAX4624EUT+TCT-ND | IC SWITCH SPDT SOT23-6 | 1
U14 | M74VHC1GT125 | M74VHC1GT125DF1GOSCT-ND | Noninverting Buffer / CMOS Logic Level Shifter | 1
U15 | M74HC4050 | 296-14529-1-ND | HEX BUFFER/CONVERTER | 1
U16 | SDCard Socket | 3M5607CT-ND | microSD Socket | 1
U17 | ADXL345 | ADXL345BCCZ-ND | 3-Axis, Digital Accelerometer | 1
U18 | LP5907 | 296-38557-1-ND | 250-mA LOW-DROPOUT LINEAR REGULATOR | 1
U19 | Inverter | NC7S14M5XCT-ND | SINGLE SCHMITT-TRIGGER INVERTER | 1
U20 | DS3234 | DS3234SN#T&RCT-ND | SPI RTC module | 1
U21 | LT1129 | LT1129IQ-5#PBF-ND | 5V Voltage Regulator | 1
U22 | LT1013 | 296-12982-1-ND | 1 MHz Op Amp | 1
U23 | LT1634 | LT1634BIS8-1.25#PBF-ND | 1.25V Shunt Regulator | 1
U24 | ADS1100-A2 | 296-14299-1-ND | Self-Calibrating 16 Bit ADC - Address A2 | 1
U25 | TS5A21366DCUR | 296-24304-1-ND | IC SWITCH DUAL SPST US8 | 1
U26 | TXB0106PWR | 296-23759-1-ND | IC 6BIT NON-INV TRANSLTR 16TSSOP | 1
HF3 | 2x3 | S7106-ND | 2x3 female header, unshrouded | 1 | **not labeled on board, see photo
HM1,HM2,HM3,HM4,HM5,HM6,HM7 | 1x8 | 952-2271-ND | 1x8 male header, unshrouded | 7 | **not labeled on board, see photo
HM8,HM9,HM10 | 1x10 | 952-1843-ND | 1x10 male header, unshrouded | 3 | **not labeled on board, see photo

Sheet: Electronics Assembly
Assembly Variant | Item Description | Purpose | Vendor | Product Number | Link | Cost | Qty Per Pack | Qty Per Float | Select? (y/n) | Cost Per Float | Qty On-Hand | Comments
All | Circuit Board (Blank PCB) | Main Circuit Board | PCB Fab Express | Pop Up 5.3 | https://ecommerce.pcbfabexpress.com/ | $247.65 | 15 | 1 | y | $16.51 | 22 | Exact Price depends on Qty and Turn Time
All | Pressure Sensor Circuit Board | Pressure Sensor Circuit Board | PCB Fab Express | Pop Up 5.3 | https://ecommerce.pcbfabexpress.com/ | $50.00 | 15 | 1 | y | $3.33 | 30 | Exact Price depends on Qty and Turn Time
All | Circuit Board Components (Approximate) | Main Circuit Board | See PCB BOM | See PCB BOM |  | $180.00 | 1 | 1 | y | $180.00 | 22 | Exact Price depends on Qty and Revision
All | Circuit Board Assembly | Main Circuit Board | Schippers and Crew | Pop Up 5.3 | http://schippersandcrew.com/ | $155.00 | 1 | 1 | y | $155.00 | 22 | Exact Price depends on Qty and Revision
All | Loctite Quick Set Epoxy | Epoxy for Mounting PAR Sensor | Amazon | 1395391 | https://www.amazon.com/Loctite-Epoxy-0-85-Fluid-Syringe-1395391/dp/B000PSAKAW | $6.65 | 1 | 0.2 | n | $0.00 |  | One enough for at least 5 PAR Sensors
All | 18-8 Stainless Narrow Fillister Screws (#6-32x5/16") | Screws for Mounting Pressure Sensor PCB | McMaster | 91737A106 | https://www.mcmaster.com/#91737a106/=1cxx20s | $5.34 | 100 | 3 | y | $0.16
All | 18-8 Stainless Internal Tooth Lock Washers (#6) | Screws for Mounting Pressure Sensor PCB | McMaster | 91757A103 | https://www.mcmaster.com/#91757a103/=1al1zqk | $2.74 | 100 | 0 | y | $0.00 |  | 3 Added to Same Item Under 'Standoffs for Main Circuit Board'
All | 18-8 Stainless Screws (M2x12mm) | Screws for Mounting Camera | McMaster | 92000A019 | https://www.mcmaster.com/#92000a019/=1cxvmim | $6.16 | 100 | 4 | n | $0.00
All | 18-8 Stainless Lock Washers (M2) | Screws for Mounting Camera | McMaster | 93925A210 | https://www.mcmaster.com/#93925a210/=1cxvmzr | $3.12 | 100 | 4 | n | $0.00
All | 18-8 Stainless Hex Standoff (M2.5x6mm) | Standoff for RockBLOCK 9603 | McMaster | 94868A161 | https://www.mcmaster.com/#94868a161/=1cxvf50 | $0.96 | 1 | 2 | y | $1.92
All | 18-8 Stainless Screws (M2.5x6mm) | Standoff for RockBLOCK 9603 | McMaster | 92000A104 | https://www.mcmaster.com/#92000a104/=1cxviey | $3.54 | 100 | 2 | y | $0.07
All | 18-8 Stainless Screws (M2.5x4mm) | Standoff for RockBLOCK 9603 | McMaster | 92000A102 | https://www.mcmaster.com/#92000a102/=1cxvjaz | $3.46 | 100 | 2 | y | $0.07
All | 18-8 Stainless Internal Tooth Lock Washers (M2.5) | Standoff for RockBLOCK 9603 | McMaster | 93925A220 | https://www.mcmaster.com/#93925a220/=1cxvg8w | $3.46 | 100 | 4 | y | $0.14
All | 18-8 Stainless Hex Standoff (#6-32x1") | Standoffs for Main Circuit Board | McMaster | 91115A133 | https://www.mcmaster.com/#91115a133/=1al1wex | $1.99 | 1 | 4 | y | $7.96
All | 18-8 Stainless Narrow Fillister Screws (#6-32x1/2") | Standoffs for Main Circuit Board | McMaster | 91737A109 | https://www.mcmaster.com/#91737a109/=1al20rw | $5.92 | 100 | 8 | y | $0.47
All | 18-8 Stainless Internal Tooth Lock Washers (#6) | Standoffs for Main Circuit Board | McMaster | 91757A103 | https://www.mcmaster.com/#91757a103/=1al1zqk | $2.74 | 100 | 11 | y | $0.30 |  | 3 Extra Added for Pressure Sensor PCB Mounting, 8 needed for Main Circuit board
All | Nylon Unthreaded Spacer, 5/8" Long for 1/4" Screw Size | Standoffs for Electronics Stack | McMaster | 94639A572 | https://www.mcmaster.com/#94639a572/=1cxwqb6 | $10.19 | 100 | 10 | y | $1.02
All | 18-8 Stainless Hex Head Screw,1/4"-20, 1-3/8" Long | Standoffs for Electronics Stack | McMaster | 92240A237 | https://www.mcmaster.com/#92240a237/=1cxvsja | $10.38 | 50 | 4 | y | $0.83
All | 18-8 Stainless Hex Head Screw,1/4"-20, 1-3/4" Long | Standoff for GPS Mount | McMaster | 92240A548 | https://www.mcmaster.com/#92240a548/=1cxx5zt | $4.88 | 25 | 1 | y | $0.20
All | Rubber Bumper with Unthreaded Hole,1.5" High, 1/4" Hole Diameter | Standoff for GPS Mount | McMaster | 9540K2 | https://www.mcmaster.com/#9540k2/=1co3wcr | $2.42 | 1 | 1 | y | $2.42
All | 18-8 Stainless Split Lock Washer, 1/4" Screw Size | Standoffs for Electronics Stack and GPS Mount | McMaster | 92146A029 | https://www.mcmaster.com/#92146a029/=1cxwqxm | $3.68 | 100 | 5 | y | $0.18 |  | 4 for electronics stack, 1 for gps mount
All | 18-8 Stainless Washer, 1/4" Screw Size | Standoffs for Electronics Stack and GPS Mount | McMaster | 92141A029 | https://www.mcmaster.com/#92141a029/=1cxwrox | $3.37 | 100 | 5 | y | $0.17 |  | 4 for electronics stack, 1 for gps mount
All | 18-8 Stainless Hex Nut, 1/4"-20 Thread Size | Standoffs for Electronics Stack and GPS Mount | McMaster | 91845A029 | https://www.mcmaster.com/#91845A029 | $4.31 | 100 | 1 | y | $0.04 |  | 1 for gps mount
All | Connector/Adaptor SMA plug, male pin to TMC jack, female socket | SMA adapter for RockBlock module to Antenna | DigiKey | ACX1327-ND | https://www.digikey.com/product-detail/en/amphenol-rf-division/242124/ACX1327-ND/1012004 | $15.17 | 1 | 1 | y | $15.17
All | CR1220 3V Lithium Cell | RTC Backup and GPS Backup | DigiKey | NO33-ND | https://www.digikey.com/product-detail/en/energizer-battery-company/CR1220VP/N033-ND/704851 | $0.97 | 1 | 2 | y | $1.94
All | SD Card 32GB, SanDisk Ultra Class 10 SDHC UHS-I Memory Card | Data Storage | Amazon | SDSDUNC-032G-GN6IN | https://www.amazon.com/SanDisk-Ultra-Class-Memory-SDSDUNC-032G-GN6IN/dp/B0143RT8OY?hvadid=198076677096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 | 6.79 | 1 | 1 | y | $6.79
 |  |  |  |  |  |  |  |  |  | $394.70 |  | TOTAL

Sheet: Mechanical Assembly
Assembly Variant | Material Description | Purpose | Vendor | Product Number | Link | Cost | Qty Per Pack | Qty Per Float | Select? (y/n) | Cost Per Float | Qty On-Hand | Comments
All | 2-256 Buna O-Ring | O-Ring - End Cap Face Seal | McMaster | 9452K357 | https://www.mcmaster.com/#9452K357 | $9.34 | 10 | 1 | y | $0.93
All | 2-163 Buna O-Ring | O-Ring - End Cap Piston Seal | McMaster | 9452K322 | https://www.mcmaster.com/#9452K322 | $10.14 | 25 | 1 | y | $0.41
All | 2-123 Buna O-Ring | O-Rings - PAR Sensor | McMaster | 9452K87 | https://www.mcmaster.com/#9452K87 | $7.05 | 100 | 2 | n | $0.00
All | 2-118 Buna O-Ring | O-Rings - Vacuum and Pressure Ports | McMaster | 9452K82 | https://www.mcmaster.com/mv1486502887/#9452k82/=16a99ei | $5.61 | 100 | 2 | y | $0.11
All | 2-126 Buna O-Ring | O-Ring - Fluorometer Face Seal | McMaster | 9452K91 | https://www.mcmaster.com/#9452k91/=1cxyt18 | $8.03 | 100 | 1 | n | $0.08
All | 2-120 Buna O-Ring | O-Ring - Fluorometer Piston Seal | McMaster | 9452K84 | https://www.mcmaster.com/#9452K84 | $6.13 | 100 | 1 | n | $0.06
All | 2-137 Buna O-Ring | O-Ring - Camera Face Seal | McMaster | 9452K143 | https://www.mcmaster.com/#9452K143 | $11.31 | 100 | 1 | n | $0.11
All | 2-131 Buna O-Ring | O-Ring - Camera Piston Seal | McMaster | 9452K136 | https://www.mcmaster.com/#9452k136/=1cxytoc | $10.32 | 100 | 1 | n | $0.10
All | Air and Water Quick-Disconnect Tube Coupling,Socket with Shut-Off Valve, 3/32 Coupling, 1/8 NPT Male | Vacuum Port | McMaster | 51605K29 | https://www.mcmaster.com/#51605k29/=169p8jh | $11.01 | 1 | 1 | y | $11.01
All | Abrasion-Resistant Polyurethane Rubber Round Tube, 1" Long, 1" OD | Frame Hardware - Spacers for Trawl Float Ears | McMaster | 9697K121 | https://www.mcmaster.com/#9697k121/=169r6zd | $4.40 | 1 | 3 | y | $13.20
All | 12" Trawl Float | Main Pressure Housing | Seattle Marine | YUN10M-8 | http://www.b2b.seamar.com/WVVAI/wvo?qid=InventoryInq2x&ItemNo=YUN10M-8 (http://www.thezincguy.com/ta-3-bolt-on-plate-zinc-anode-trim-tab) | $36.68 | 1 | 1 | y | $36.68
 |  |  |  |  |  |  |  |  |  | $62.70 |  | TOTAL Float
DBV Tech Burn Wire Release | 304 Stainless Steel Bolt-Together Framing - 1 ft length | Frame Hardware - Main Frame | McMaster | 3414T11 | https://www.mcmaster.com/#3414t11/=1comtna | $5.12 | 1 | 4 | y | $20.48
DBV Tech Burn Wire Release | 304 Stainless Steel Bolt-Together Framing - 3 ft length | Frame Hardware - Main Frame | McMaster | 3414T11 | https://www.mcmaster.com/#3414t11/=1comtna | $13.91 | 1 | 1 | y | $13.91
DBV Tech Burn Wire Release | 18-8 Stainless Hex Head Screw,5/16"-18, 1-3/4" Long, Partially Threaded | Frame Hardware - Main Frame | McMaster | 92198A689 | https://www.mcmaster.com/#92198a689/=1d7375v | $7.07 | 25 | 3 | y | $0.85
DBV Tech Burn Wire Release | 18-8 Stainless Hex Head Screw,5/16"-18, 2" Long, Partially Threaded | Frame Hardware - Attaching Anodes | McMaster | 92198A691 | https://www.mcmaster.com/#92198a691/=1d737np | $7.80 | 25 | 2 | y | $0.62
DBV Tech Burn Wire Release | 18-8 Stainless Split Lock Washer, 5/16" Screw Size | Frame Hardware - Main Frame | McMaster | 92146A030 | https://www.mcmaster.com/#92146a030/=1d7384y | $5.51 | 100 | 6 | y | $0.33
DBV Tech Burn Wire Release | 18-8 Stainless Washer, 5/16" Screw Size | Frame Hardware - Main Frame | McMaster | 92141A030 | https://www.mcmaster.com/#92141a030/=1d738ka | $5.10 | 100 | 12 | y | $0.61
DBV Tech Burn Wire Release | 18-8 Stainless Hex Nuts, 5/16" Screw Size | Frame Hardware - Main Frame | McMaster | 91845A030 | https://www.mcmaster.com/#91845A030 | $5.77 | 100 | 6 | y | $0.35
DBV Tech Burn Wire Release | 18-8 Stainless Steel Oversized Washer, for 5/16" Screw Size, 0.344" ID, 1.25" OD | Frame Hardware - Main Frame | McMaster | 90313A111 | https://www.mcmaster.com/#90313a111/=1ddt9bo | $6.57 | 25 | 4 | y | $1.05
 |  |  |  |  |  |  |  |  |  | $38.20 |  | TOTAL Release
 |  |  |  |  |  |  |  |  |  | $100.90 |  | TOTAL ALL
DBV Tech Burn Wire Release | 18-8 Stainless Steel Oversized Washer, for 5/16" Screw Size, 0.344" ID, 1.5" OD ZINC PLATED STEEL | Frame Hardware - Trawl Float Ears | McMaster | 91090A111 (https://www.mcmaster.com/90313A110) | https://www.mcmaster.com/91090A111 | 9.6 | 25 | 4 | y
DBV Tech Burn Wire Release | 18-8 Stainless Hex Head Screw,5/16"-18, 4" Long, Partially Threaded | Frame Hardware - Trawl Float Ears | McMaster | 92198A699 (https://www.mcmaster.com/92198A699) | https://www.mcmaster.com/92198a699 | 6.28 | 10 | 4 | y

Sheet: Machine Shop Parts
Assembly Variant | Filename of Part | Qty Per Float | Purpose | Material Description | Vendor for Material | Link | Approx Material Cost | Select?(y/n) | Approx Machining Hours | Approx Machining Cost | Qty On-Hand | Comments | Machining Hourly Cost
All | {FOCI}{PopUp}{End Cap}{2} | 1 | End Cap Material | Black Delrin® Acetal Resin | McMaster | https://www.mcmaster.com/#8575k633/=169p0ux | $60.00 | y | 1.8 | $137.50 |  | One 24"x24" sheet can make 9 end caps, delrin sheets also have no problems with centerline porosity like rounds sometimes do | $75.00
All | {FOCI}{PopUp}{TAGPARQ Acryllic Housing}{1} | 1 | Housing for PAR Sensor | Cast Clear Acryllic | McMaster |  | $2.00 | n | 0.7 | $0.00 |  | -
All | {FOCI}{PopUp}{Camera Housing}{1} | 1 | Housing for Camera | Cast Clear Acryllic | McMaster |  | $4.00 | n | 1.0 | $0.00 |  | -
All | {FOCI}{PopUp}{Pressure Sensor Mount}{1} | 1 | Housing for Pressure Sensor | Black Delrin® Acetal Resin | McMaster |  | $5.00 | y | 0.8 | $56.25 |  | -
All | {FOCI}{PopUp}{VacuumPortCap}{1} | 1 | Housing to Seal Vacuum Port | Black Delrin® Acetal Resin | McMaster |  | $5.00 | y | 0.3 | $25.00 |  | -
All | {FOCI}{PopUp}{PCB Circular Mount}{1} | 1 | Supporting PCB and Antennas | 0.12" Nominal Thickness 304 Stainless | McMaster |  | $10.00 | y | 0.7 | $50.00 |  | -
All | {FOCI}{PopUp}{Trawl Float 12 Inch}{2} | 1 | Main Pressure Housing | 12" Trawl Float | Seattle Marine | http://www.b2b.seamar.com/WVVAI/wvo?qid=InventoryInq2x&ItemNo=YUN10M-8 | see Mechanical Assembly | y | 0.9 | $68.75 |  | -
All |  | 1 | Fluorometer Dummy Plug | Black Delrin® Acetal Resin | McMaster |  | $15.00 | y | 2.8 | $206.25
With Fluorometer | {FOCI}{PopUp}{FluorometerHousing}{1} | 1 | Fluorometer Housing | Black Delrin® Acetal Resin | McMaster |  | $15.00 | n | 2.8 | $0.00
All |  | 1 | Counterbalance | Steel |  |  |  | y |  | $0.00
 |  |  |  |  |  |  | $95.00 | TOTAL Materials |  | $543.75 |  | TOTAL Machining
 |  |  |  |  |  |  |  |  | $638.75 | TOTAL ALL

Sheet: Single Item Costs
Item Description | Purpose | Vendor | Product Number | Link | Cost | Qty Per Pack | Qty on Hand | Qty NEEDED | Single Item Cost | Comments
MityVac Silverline Pump | Handheld Vacuum Pump | Amazon | MV8510 | https://www.amazon.com/Mityvac-MV8510-Silverline-Elite-Hand/dp/B004IQM460?s=automotive | $57.12 | 1 | 3 | 0 | $0.00 | Alumium/Zinc Version for Durability. Not PVC version
Plastic Quick-Disconnect Tube Coupling for Air and Water (Plug, 3/32 Coupling Size, for 1/8" Barbed Tube ID) | Plug for Vacuum Pump Fitting | McMaster | 51605K12 | https://www.mcmaster.com/#51605K12 | $2.02 | 1 | 3 | 0 | $0.00
Abrasion-Resistant Polyurethane Tubing (for Fuels, 1/8" ID, 3/8" OD) | 1/8" Tubing for Vacuum pump | McMaster | 5792K51 | https://www.mcmaster.com/#5792K51 | $3.56 | 1 | 3 | 0 | $0.00 | 1/8" for quick-disconnect fitting, 'fuel' tubing for use in moist environments. Will also work for air
Abrasion-Resistant Polyurethane Tubing (for Fuels, 1/4" ID, 7/16" OD) | 1/4" Tubing for Vacuum pump | McMaster | 5792K36 | https://www.mcmaster.com/#5792K36 | $2.97 | 1 | 3 | 0 | $0.00 | 1/4" for pump fitting, 'fuel' tubing for use in moist environments. Will also work for air
Moisture-Resistant Acetal Barbed Tube Fitting (Reducing Straight for 1/4" x 1/8" Tube ID) | Reducing Adapter for Vacuum Pump Tubing | McMaster | 5047K25 | https://www.mcmaster.com/#5047K25 | $1.46 | 1 | 3 | 0 | $0.00
 |  |  |  |  |  |  |  |  | $0.00 | TOTAL Vacuum Pump
Fluorometer Calibration Solution, Rhodamine WT 400 ppb Chlorophyll Calibration Standard, 1 Liter | Fluorometer Calibration | Turner Designs | 6500-120 | https://www.turnerdesigns.com/product-page/400-ppb-rhodamine-wt | $129.00 | 1L | 0 | 1 | $129.00
DBV Tech Burn Wire Release | Re-arming Kits | DBV Technologies |  |  | $95.00 | 1 | 4 | 0
 |  |  |  |  |  |  |  |  | $129.00 | TOTAL OTHER
 |  |  |  |  |  |  |  |  | $129.00 | TOTAL SINGLE ITEM COSTS

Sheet: Release Mechanism
Assembly Variant | Item Description | Purpose | Vendor | Product Number | Link | Cost | Qty Per Pack | Qty Per Float | Cost Per Float | Qty On-Hand | Comments
DBV Tech Burn Wire Release | Underwater Release Black Delrin Release Block | Burn Wire | DBV Technologies | (Model DBV-BW-RBA-02C) |  | $167.25 | 1 | 1 | $167.25
DBV Tech Burn Wire Release | Release Controller Electronics Board | Burn Wire | DBV Technologies |  |  | $95.25 | 1 | 1 | $95.25
DBV Tech Burn Wire Release | 17" Cable Penetrator Overmold | Burn Wire | DBV Technologies | Brass 7/16-20x1in Bulkhead Penetrator w/ In -Line XSA Connector |  | $322.50 | 1 | 1 | $322.50
 |  |  |  |  |  |  |  |  | $585.00 |  | TOTAL

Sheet: TOTAL COSTS
Spending Category | COST PER FLOAT | FLOAT BUILD Qty | TOTAL COSTS by Category
Sensors and Comms | $635.83 | 25 | $15895.71
Battery | $133.13 |  | $3328.25
Electronics Assembly | $394.70 |  | $9867.43
Mechanical Assembly | $100.90 |  | $2522.55
Machine Shop Parts | $638.75 |  | $15968.75
Single Item Costs | $5.16 |  | $129.00
Release Mechanism | $585.00 |  | $14625.00
TOTAL COST PER FLOAT | $2493.47 | TOTAL COST FOR BUILD | $62336.69

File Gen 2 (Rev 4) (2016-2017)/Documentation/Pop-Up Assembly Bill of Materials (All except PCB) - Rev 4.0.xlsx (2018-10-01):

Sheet: Mechanical Assembly
Material Description | Purpose | Vendor | Product Number | Link | Cost | Qty Per Pack | Qty Per Float | Cost Per Float | Comments
Abrasion-Resistant Polyurethane Rubber Round Tube, 1" Long, 1" OD | Frame Hardware - Spacers for Trawl Float Ears | McMaster | 9697K121 | https://www.mcmaster.com/#9697k121/=169r6zd | $4.40 | 1 | 2 | $8.80
Electrical-Insulating Nylon 6/6 Sleeve Washer for 1/4" Screw Size, 0.188" Overall Height | Frame Hardware - Isolators, Single sheet thickness | McMaster | 91145A162 | https://www.mcmaster.com/mv1486502887/#91145a162/=169pa16 | $6.42 | 100 | 6 | $0.39
Electrical-Insulating Nylon 6/6 Sleeve Washer for 1/4" Screw Size, 0.313" Overall Height | Frame Hardware - Isolators, Double sheet thickness | McMaster | 91145A165 | https://www.mcmaster.com/#91145a165/=169qy87 | $5.93 | 100 | 4 | $0.24
316 Stainless Steel Washer for 1/4" Screw Size, 0.281" ID, 0.625" OD | Frame Hardware - Washers | McMaster | 90107A029 | https://www.mcmaster.com/#90107a029/=169r0ig | $7.45 | 100 | 22 | $1.64 | Extra Washers needed to fill small gap on burn wire release mounts (Included in qty)
316 Stainless Steel Split Lock Washer, for 1/4" Screw Size, 0.26" ID, 0.487" OD | Frame Hardware - Lock Washers | McMaster | 92147A029 | https://www.mcmaster.com/mv1486502887/#92147a029/=169p7p9 | $4.57 | 100 | 14 | $0.64
Super-Corrosion-Resistant 316 Stainless Steel Hex Nut, 1/4"-20 Thread Size | Frame Hardware - Hex Nuts | McMaster | 94804A029 | https://www.mcmaster.com/#94804a029/=169p5wk | $7.21 | 100 | 14 | $1.01
Super-Corrosion-Resistant 316 Stainless Steel Hex Head Screw, 1/4"-20 Thread Size, 2" Long, Partially Threaded | Frame Hardware - 2" Hex Cap Screws | McMaster | 92186A550 | https://www.mcmaster.com/#92186a550/=169qwo2 | $3.82 | 10 | 4 | $1.53
Super-Corrosion-Resistant 316 Stainless Steel Hex Head Screw, 1/4"-20 Thread Size, 1-3/4" Long, Partially Threaded | Frame Hardware - 1-3/4" Hex Cap Screws | McMaster | 92186A548 | https://www.mcmaster.com/#92186a548/=169p45y | $3.70 | 10 | 10 | $3.70
18-8 Stainless Steel Cotter Pin, 1/16" Diameter, 1" Length | Frame Hardware - Release Hinge Cotter Pin | McMaster | 98401A417 | https://www.mcmaster.com/#98401a417/=169p4y6 | $2.63 | 100 | 1 | $0.03
18-8 Stainless Steel Clevis Pin, 1/4" Diameter, 1-1/2" Length, 1-5/16" Usable Length | Frame Hardware - Release Hinge | McMaster | 92390A163 | https://www.mcmaster.com/#92390a163/=169p4hf | $11.12 | 10 | 1 | $1.11
Air and Water Quick-Disconnect Tube Coupling,Socket with Shut-Off Valve, 3/32 Coupling, 1/8 NPT Male | Vacuum Port | McMaster | 51605K29 | https://www.mcmaster.com/#51605k29/=169p8jh | $11.01 | 1 | 1 | $11.01
Vibration-Damping Clamp with TPR Cushion, 304 Stainless Steel, 1-1/16" ID | Frame Hardware - Burn Wire Mounting Clamps | McMaster | 11355T82 | https://www.mcmaster.com/#11355t82/=169r2wn | $5.25 | 1 | 2 | $10.50
Harsh-Environment Cable Tie, Long Lasting, Ultra-UV-Resistant Nylon, 8" Long | Frame Hardware - Release Clip | McMaster | 70215K96 | https://www.mcmaster.com/#70215k96/=169r5bi | $7.38 | 10 | 1 | $0.74
Type 302 Stainless Steel Extension Spring, 2.0" Length, .375" OD, .048" Wire Diameter | Frame Hardware - Release Spring | McMaster | 94135K14 | https://www.mcmaster.com/mv1486502887/#94135k14/=169r98q | $4.84 | 3 | 1 | $1.61
Stainless Steel Extension Spring Anchor Stud, Standard, 1/4"-20 Thread, 1-1/4" Overall Length | Frame Hardware - Release Spring Anchors | McMaster | 95907A480 | https://www.mcmaster.com/mv1486502887/#95907a480/=169r8mi | $6.42 | 1 | 2 | $12.84
Closed Eye Routing Eyebolt - Not for Lifting, 316 Stainless Steel with Nut, 10-24 Thread Size, 2" Shank Length | Frame Hardware - Release Eye Bolt | McMaster | 9494T31 | https://www.mcmaster.com/#9494t31/=169ra1q | $6.21 | 1 | 1 | $6.21
2-256 | O-Rings - End Cap Face Seal | McMaster | 9452K357 | https://www.mcmaster.com/mv1486502887/#9452k357/=16a991z | $9.34 | 10 | 1 | $0.93
2-163 | O-Rings - End Cap Piston Seal | McMaster | 9452K322 | https://www.mcmaster.com/mv1486502887/#9452k322/=16a9971 | $10.14 | 25 | 1 | $0.41
2-123 | O-Rings - PAR Sensor | McMaster | 9452K87 | https://www.mcmaster.com/mv1486502887/#9452k87/=16a99cj | $6.80 | 100 | 2 | $0.14
2-118 | O-Rings - Vacuum and Pressure Ports | McMaster | 9452K82 | https://www.mcmaster.com/mv1486502887/#9452k82/=16a99ei | 5.61 | 100 | 3 | $0.17
Polypropylene Unthreaded Spacers,1/2" OD, 1" Long | Spacer for Anodes | McMaster | 94729A260 | https://www.mcmaster.com/#94729a260/=1874va4 | $8.36 | 10 | 4 | $3.34
316 Stainless Steel Washer Oversized, 1/4" Screw Size, 0.266" ID, 0.875" OD | Oversized Washer for Anodes | McMaster | 91525A119 |  | $8.19 | 25 | 8 | $2.62
 |  |  |  |  |  |  |  | $69.60

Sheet: Machine Shop Parts
Filename of Part | Qty Per Float | Material Description | Purpose | Vendor | Product Number | Link | Approx Cost | Comments
{FOCI}{PopUp}{Trawl Float 12 Inch}{1} | 1 | 12" Trawl Float | Pressure Housing | Seattle Marine | YUN10M-8 | http://www.b2b.seamar.com/WVVAI/wvo?qid=InventoryInq2x&ItemNo=YUN10M-8 | - | -
{FOCI}{PopUp}{End Cap}{1} | 1 | 2" Black Delrin Sheet | End Cap Material | McMaster | 8575K633 | https://www.mcmaster.com/#8575k633/=169p0ux | - | One 24"x24" sheet can make 9 end caps, delrin sheets also have no problems with centerline porosity like rounds sometimes do
{FOCI}{PopUp}{Bottom Bracket Bottom Spacer}{1} | 1 | Black Delrin for Frame Pieces | Frame Hardware - Frame Material | McMaster | 8528K36 | https://www.mcmaster.com/mv1486502887/#=16a9d93 | - | -
{FOCI}{PopUp}{Bottom Bracket Release Bar}{1} | 1 | Black Delrin for Frame Pieces | Frame Hardware - Frame Material | McMaster | 8528K36 | https://www.mcmaster.com/mv1486502887/#=16a9d93 | - | -
{FOCI}{PopUp}{Link 886 Modified Delrin}{1} | 1 | Black Delrin for Frame Pieces | Frame Hardware - Frame Material | McMaster | 8528K36 | https://www.mcmaster.com/mv1486502887/#=16a9d93 | - | -
{FOCI}{PopUp}{Bottom Bracket Top Spacer}{1} | 1 | Black Delrin for Frame Pieces | Frame Hardware - Frame Material | McMaster | 8528K36 | https://www.mcmaster.com/mv1486502887/#=16a9d93 | - | -
{FOCI}{PopUp}{Bottom Bracket T-Bar}{1} | 2 | Black Delrin for Frame Pieces | Frame Hardware - Frame Material | McMaster | 8528K36 | https://www.mcmaster.com/mv1486502887/#=16a9d93 | - | -
{FOCI}{PopUp}{Bottom Bracket Bottom Spacer}{1} | 1 | Black Delrin for Frame Pieces | Frame Hardware - Frame Material | McMaster | 8528K36 | https://www.mcmaster.com/mv1486502887/#=16a9d93 | - | -
{FOCI}{PopUp}{Bottom Bracket Vertical}{1} | 2 | Highly Corrosion-Resistant 5086 Aluminum, Sheet, .125" Thick | Frame Hardware - Frame Material | McMaster | 5865T73 | https://www.mcmaster.com/#5865t73/=169qvc3 | - | -
{FOCI}{PopUp}{Bottom Bracket Vee}{1} | 2 | Highly Corrosion-Resistant 5086 Aluminum, Sheet, .125" Thick | Frame Hardware - Frame Material | McMaster | 5865T73 | https://www.mcmaster.com/#5865t73/=169qvc3 | - | -
{FOCI}{PopUp}{TAGPARQ Acryllic Housing}{1} | 1 | Acryllic for PAR sensor | Frame Hardware - Frame Material | McMaster | https://www.mcmaster.com/mv1486502887/#acrylic/=16a9dse | https://www.mcmaster.com/mv1486502887/#acrylic/=16a9dse | - | -
{FOCI}{PopUp}{Steel Thermistor Plug 1_16 SAE}{1} | 1 | 1/16-27 Square Pipe Plug | Housing for Thermistor (Temp Sensor) | Delta Fastener | (001) PPQ188006 | http://www.deltafastener.com/socket-plugs-square-plugs.html | - | Min $25 order
{FOCI}{PopUp}{Pressure Sensor Mount}{1} | 2 |  |  |  |  |  | - | -
{FOCI}{PopUp}{VacuumPortCap}{1} | 1 |  |  |  |  |  | - | -
{FOCI}{PopUp}{PCB Frame}{1} | 1 |  |  |  |  |  | - | -
{FOCI}{PopUp}{AR-7 Zinc Anode}{1} | 2 | AR-7 Bolt On Drilled Plate Zinc | Anodes (Also Ballast Weight) | Deep Blue Yacht Supply | AR-7 | https://www.deepblueyachtsupply.com/ar7-zimar-plate-zinc-anode | - | -
 |  |  |  |  |  |  | 0
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

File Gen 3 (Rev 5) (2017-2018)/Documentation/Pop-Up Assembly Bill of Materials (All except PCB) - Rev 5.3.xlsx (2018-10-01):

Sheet: Sensors and Comms
Assembly Variant | Item Description | Purpose | Vendor | Product Number | Link | Cost | Qty Per Pack | Qty Per Float | Cost Per Float | Comments
All | TAG-PARQ Sensor | PAR Sensor | Skye Instruments | TAG-PARQ | katie@skyeinstruments.com, adam@skyeinstruments.com | £270.00 | 1 | 1 | $364.50 | Exchange Rate 1GBP= __ USD --->>> | 1.35
All | 10 bar Pressure Sensor | Pressure Sensor | Keller | PA4LD/81974.30/10Bar | http://www.keller-druck.com/home_e/paprod_e/4ld_e.asp | $117.75 | 1 | 1 | $117.75
All | Topside Temperature Probe | Temperature Probe | US Sensor | USP19572 REV A | http://www.ussensor.com/h2081-npt-stainless-steel | $67.00 | 1 | 1 | $67.00
All | SST Temperature Probe | Temperature Probe | US Sensor | USP19504 REV NONE | http://www.littelfuse.com/products/temperature-sensors/thermistor-probes-and-assemblies/threaded-housings/h6268.aspx | $67.00 | 1 | 1 | $67.00
All | u-CAM-III | Camera | Digikey | UCAM-III | https://www.digikey.com/product-detail/en/4d-systems-pty-ltd/UCAM-III/1613-1369-ND/6623663 | $49.98 | 1 | 1 | $49.98
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

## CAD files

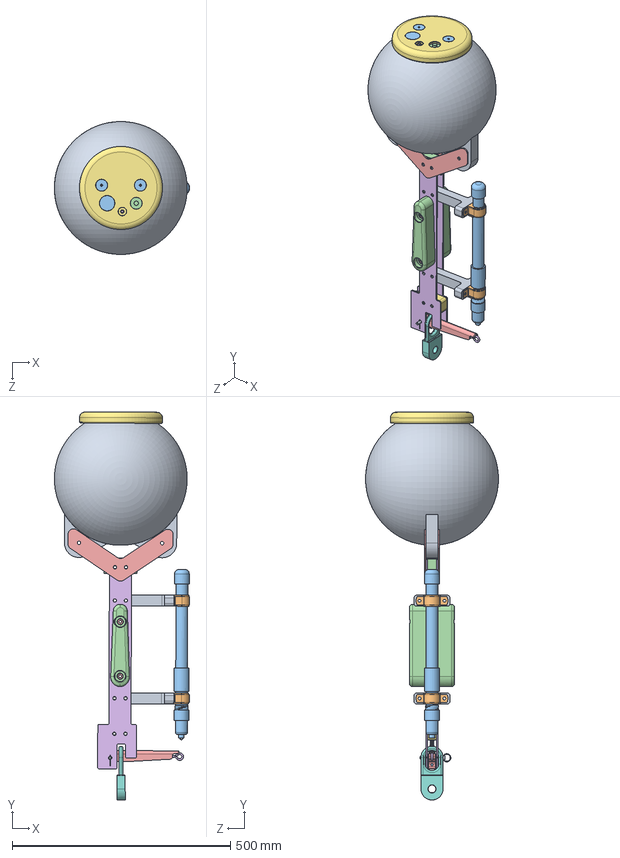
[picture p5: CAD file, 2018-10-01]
Gen 2 (Rev 4) (2016-2017)/Mechanical/Solidworks Files/{FOCI}{PopUp}{Full Assembly}{1}.SLDASM
310.1 x 889.5 x 304.8 mm
{FOCI}{PopUp}{Trawl Float 12 Inch}{1}
{FOCI}{PopUp}{TAGPARQ Sensor}{1}
{FOCI}{PopUp}{Pressure Sensor Mount}{1} x 2
{FOCI}{PopUp}{GPS Antenna}{1}
{FOCI}{PopUp}{Iridium Antenna}{1}
{FOCI}{PopUp}{Steel Thermistor Plug 1_16 SAE}{1}
{FOCI}{PopUp}{End Cap}{1}
{FOCI}{PopUp}{Vacuum Port McMaster 51605K29}{1}
{FOCI}{PopUp}{PCB Frame}{1}
{FOCI}{PopUp}{PCB Stack}{1}
{FOCI}{PopUp}{TAGPARQ Acryllic Housing}{1}
{FOCI}{PopUp}{VacuumPortCap}{1}
{FOCI}{PopUp}{Bottom Bracket Vee}{1} x 2
{FOCI}{PopUp}{Bottom Bracket Vertical}{1} x 2
{FOCI}{PopUp}{BatteryPack_12Cell_9V}{1}
{FOCI}{PopUp}{Bottom Bracket RubberBumper}{1} x 2
{FOCI}{PopUp}{Bottom Bracket T-Bar}{1} x 2
{FOCI}{PopUp}{Release Mounting Clamp}{1} x 2
{FOCI}{PopUp}{Burn Wire Release New}{1}
{FOCI}{PopUp}{Bottom Bracket Top Spacer}{1}
{FOCI}{PopUp}{Bottom Bracket Release Bar}{1}
9494T310_CLOSED EYE ROUTING EYEBOLT - NOT FOR LIFTING
{FOCI}{PopUp}{Bottom Bracket Bottom Spacer}{1}
{FOCI}{PopUp}{Link 886 Modified Delrin}{1}
92393A260_ALUMINUM CLEVIS PIN WITH COTTER PIN
extension spring 94135K14
Anchor stud blank x 2
{FOCI}{PopUp}{AR-7 Zinc Anode}{1} x 2
{FOCI}{PopUp}{94639A506_NYLON UNTHRD SPACERS}{1} x 4

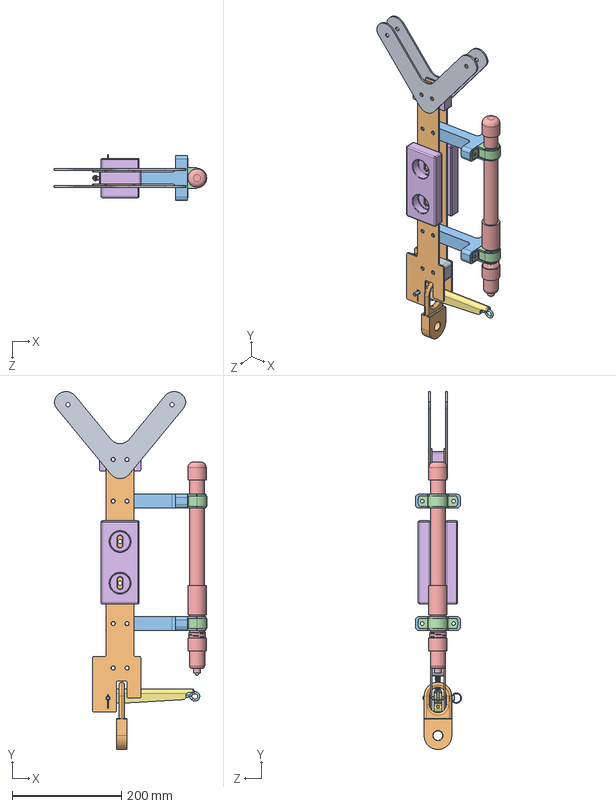
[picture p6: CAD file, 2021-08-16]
Engineering/Mechanical/Pop Up/Frame for Sub Sea Sonics Burn Wire.sldasm
279.3 x 655.5 x 84.5 mm
{FOCI}{PopUp}{Bottom Bracket Vee}{2} x 2
{FOCI}{PopUp}{Bottom Bracket Vertical}{2} x 2
{FOCI}{PopUp}{Bottom Bracket T-Bar}{1} x 2
{FOCI}{PopUp}{Release Mounting Clamp}{1} x 2
{FOCI}{PopUp}{Burn Wire Release New}{1}
{FOCI}{PopUp}{Bottom Bracket Top Spacer}{1}
{FOCI}{PopUp}{Bottom Bracket Release Bar}{1}
9494T310_CLOSED EYE ROUTING EYEBOLT - NOT FOR LIFTING
{FOCI}{PopUp}{Bottom Bracket Bottom Spacer}{1}
{FOCI}{PopUp}{Link 886 Modified Delrin}{1}
92393A260_ALUMINUM CLEVIS PIN WITH COTTER PIN
extension spring 94135K14
Anchor stud blank x 2
{FOCI}{PopUp}{TA-3 Bolt On Zic Anode}{1} x 2

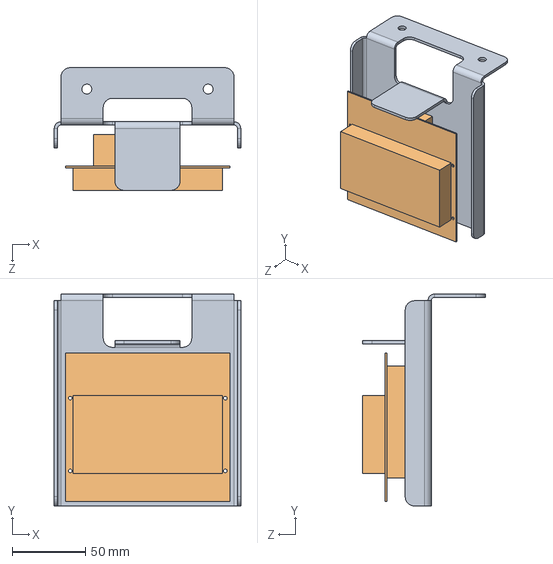
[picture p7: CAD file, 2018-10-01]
Gen 2 (Rev 4) (2016-2017)/Mechanical/Solidworks Files/{FOCI}{PopUp}{PCB Stack and Frame}{1}.SLDASM
127.0 x 144.3 x 83.6 mm
{FOCI}{PopUp}{PCB Frame}{2}
{FOCI}{PopUp}{PCB Stack}{1}

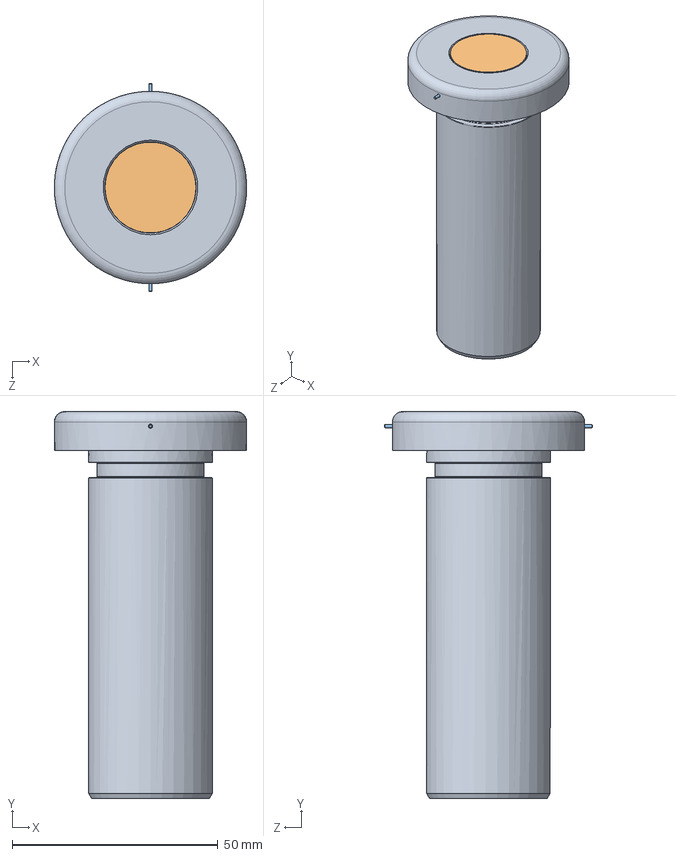
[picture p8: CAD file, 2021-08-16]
Engineering/Mechanical/Gen 3/{FOCI}{PopUp}{Fluorometer In Housing}{1}.SLDASM
46.7 x 94.0 x 50.4 mm
{FOCI}{PopUp}{FluorometerHousing}{1}
{FOCI}{PopUp}{Turner Cyclops Fluorometer}{1}
97395A366_CORROSION RESISTANT DOWEL PIN x 2

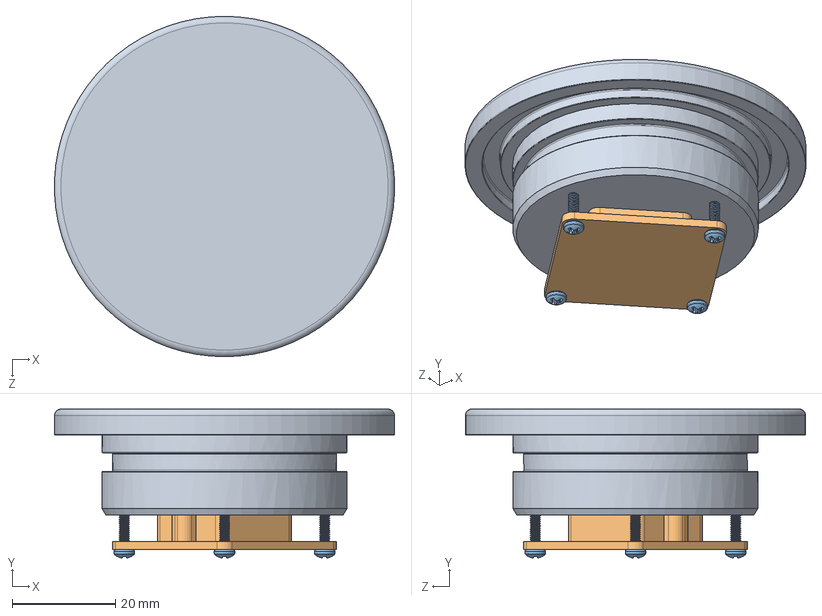
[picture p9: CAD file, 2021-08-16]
Engineering/Mechanical/Pop Up/{FOCI}{PopUp}{Camera In Housing}{1}.SLDASM
66.0 x 28.9 x 66.0 mm
{FOCI}{PopUp}{CameraHousing}{1}
{FOCI}{PopUp}{UCAMIII}{2}
92000A019_18-8 SS METRIC PAN HEAD PHIL MACHINE SCREW(1) x 4

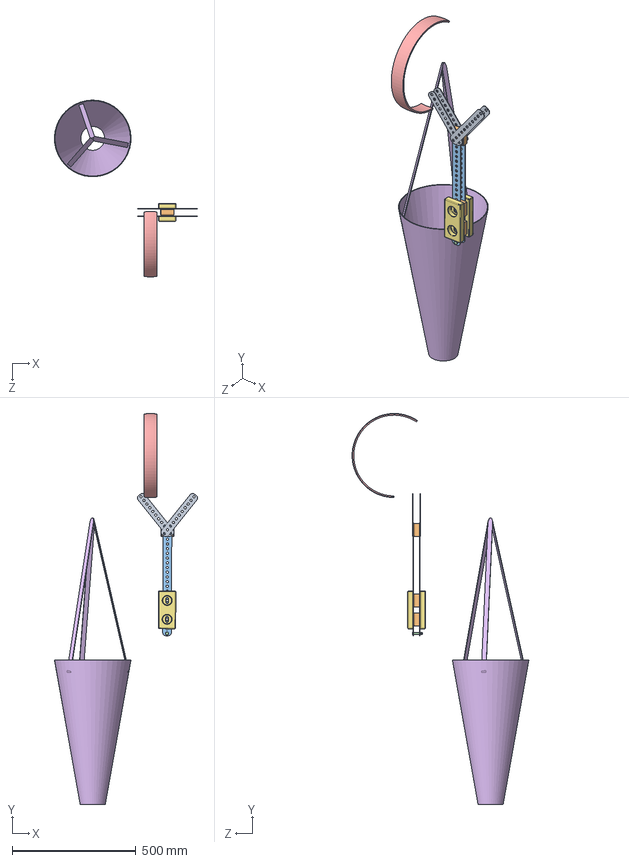
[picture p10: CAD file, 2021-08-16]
Engineering/Mechanical/Pop Up/Frame for Galvanic Release or DBVTech Burn Wire.sldasm
578.8 x 1581.1 x 715.0 mm
{FOCI}{PopUp}{Bolt Together Framing 8 inch Section}{1} x 4
{FOCI}{PopUp}{Square Rubber Bumper 9306K44}{1} x 3
{FOCI}{PopUp}{Bolt Together Framing 18 inch Section}{1} x 2
92401A212_316 STAINLESS STEEL CLEVIS PIN
{FOCI}{PopUp}{Cloth Cover}{1}
{FOCI}{PopUp}{TA-3 Bolt On Zic Anode}{1} x 2

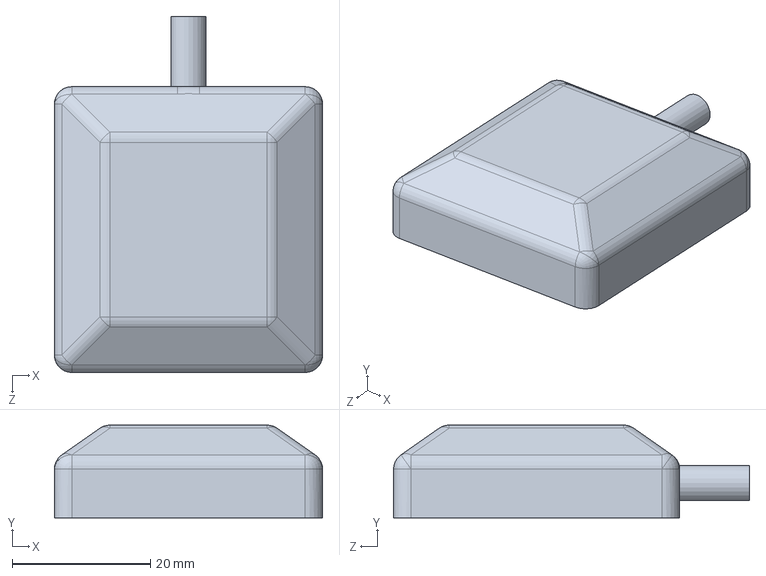
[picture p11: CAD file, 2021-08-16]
Engineering/Mechanical/Gen 3/{FOCI}{PopUp}{GPS Antenna}{1}.SLDPRT
38.9 x 13.5 x 51.6 mm

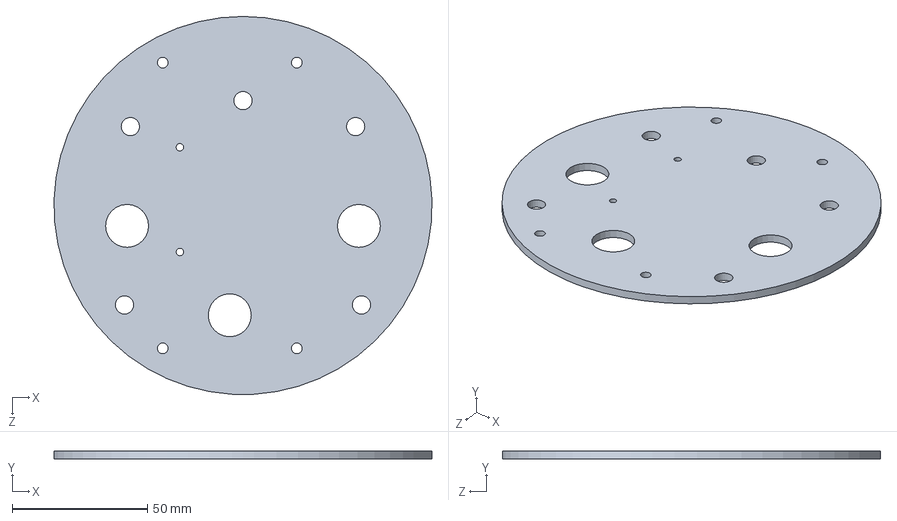
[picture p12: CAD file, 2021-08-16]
Engineering/Mechanical/Pop Up/{FOCI}{PopUp}{PCB Circular Mount}{1}.SLDPRT
139.6 x 3.05 x 139.7 mm

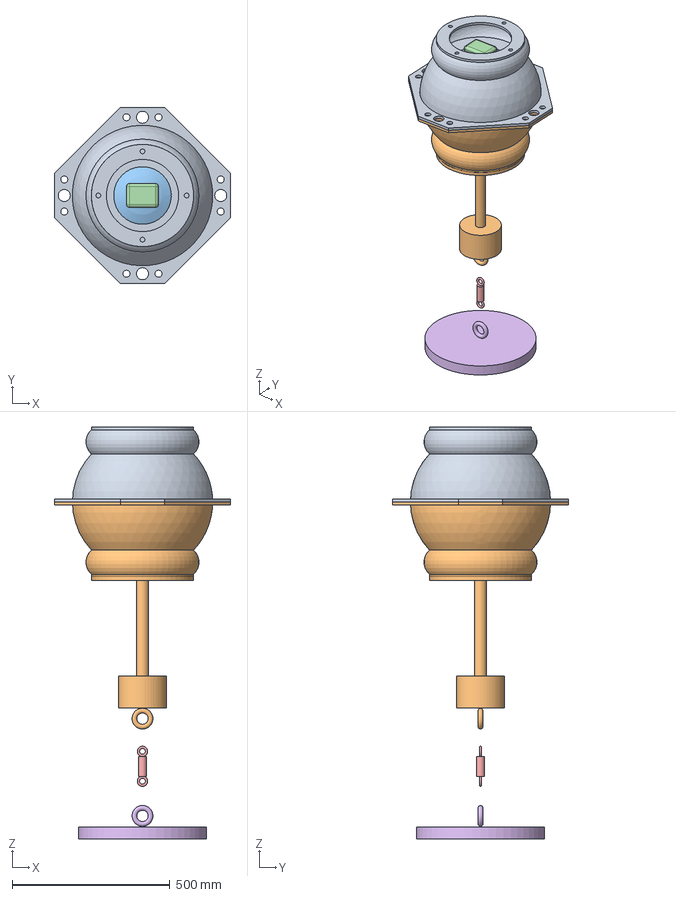
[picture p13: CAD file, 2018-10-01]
Gen 1 (Sat Tag Prototype) (Deployed July 2015 Healy)/Concept Drawings/FreeCAD/buoy design 1/buoy design 1.FCStd
558.8 x 558.8 x 1304.4 mm
TopShell
WholeBuoy
Buoy
SatTag
GTRWhole
AnchorWhole

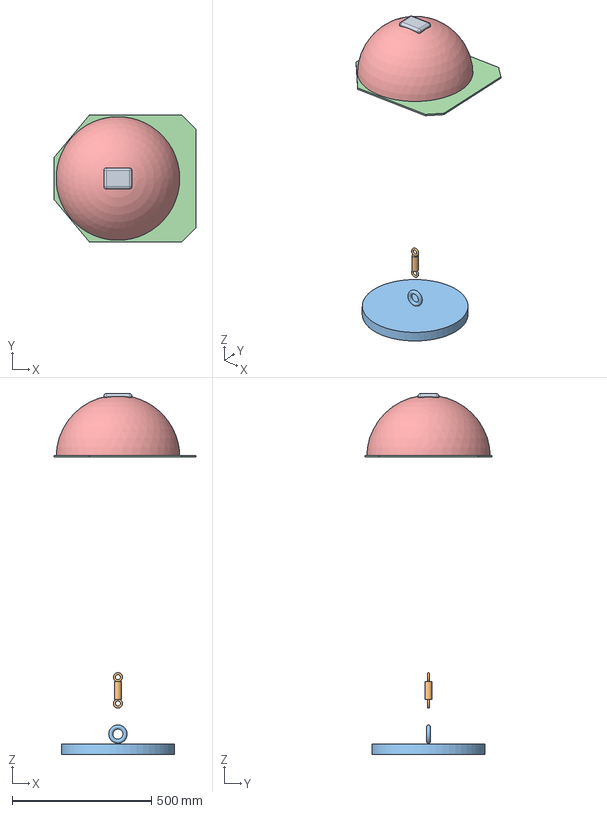
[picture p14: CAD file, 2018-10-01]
Gen 1 (Sat Tag Prototype) (Deployed July 2015 Healy)/Concept Drawings/FreeCAD/buoy design 2/buoy design 2.FCStd
508.0 x 457.2 x 1295.4 mm
SatTag
GTRWhole
AnchorWhole

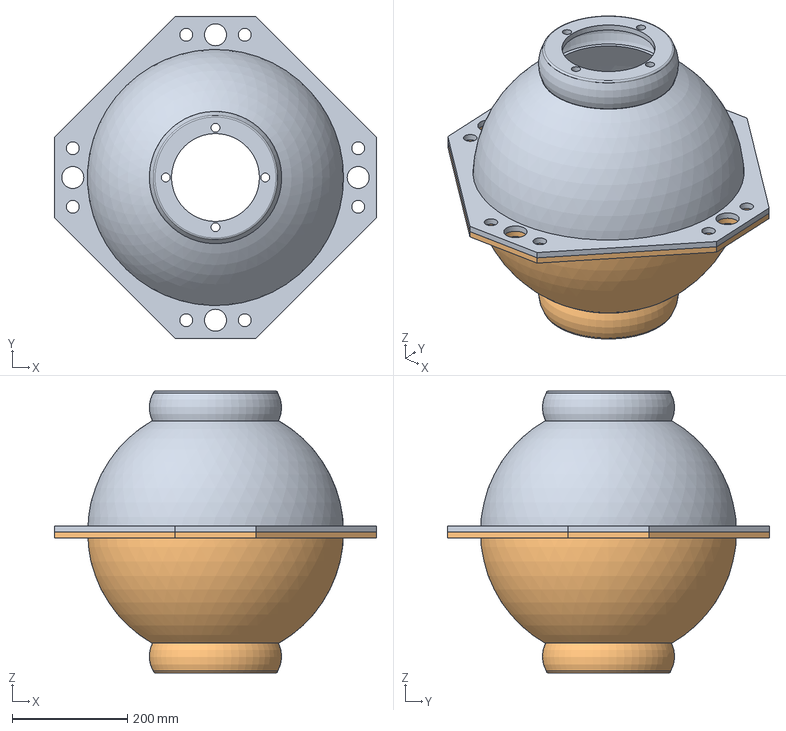
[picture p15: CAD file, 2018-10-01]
Gen 1 (Sat Tag Prototype) (Deployed July 2015 Healy)/Concept Drawings/FreeCAD/hard hat both sides.FCStd
558.8 x 558.8 x 488.9 mm
Fillet (Mirror #1)

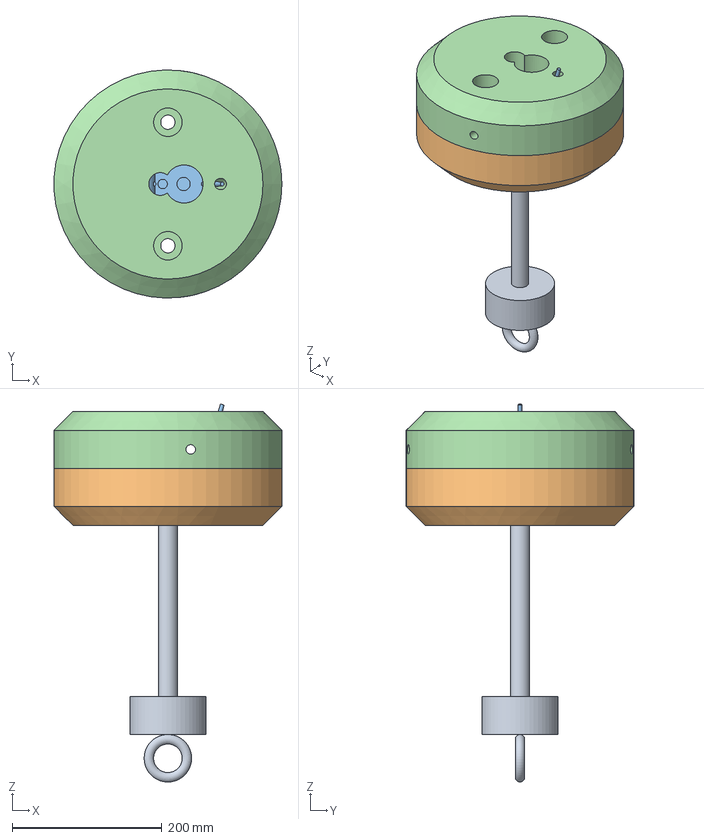
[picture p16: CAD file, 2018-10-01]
Gen 1 (Sat Tag Prototype) (Deployed July 2015 Healy)/Concept Drawings/FreeCAD/SDRL Syntatic/orginial syntactic design.FCStd
304.5 x 304.7 x 505.2 mm
CounterWt
BottomHalfBoltsCutout
SDRLNew
TopHalfComplete

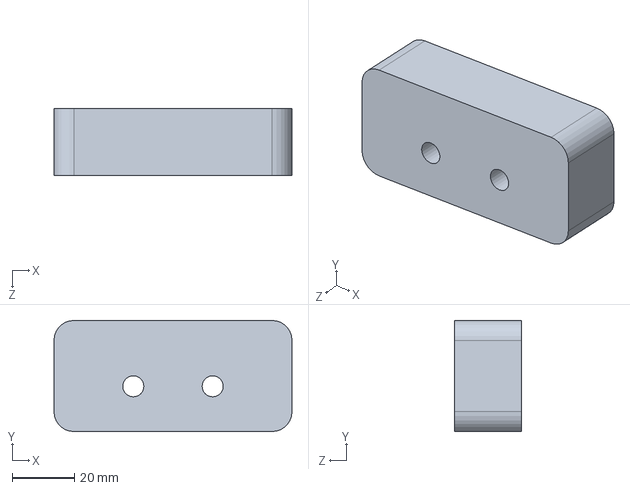
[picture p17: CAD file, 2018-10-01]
Gen 2 (Rev 4) (2016-2017)/Mechanical/Solidworks Files/{FOCI}{PopUp}{Bottom Bracket Bottom Spacer}{1}.SLDPRT
76.2 x 35.6 x 21.6 mm

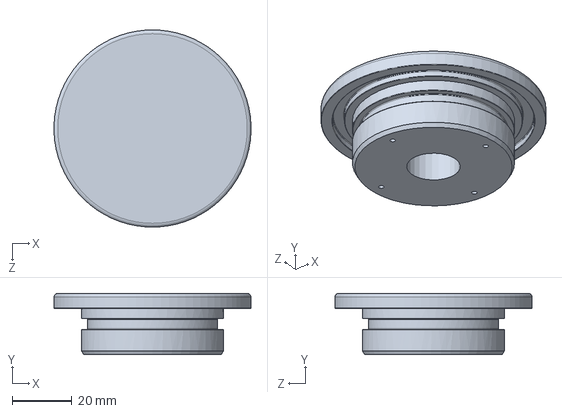
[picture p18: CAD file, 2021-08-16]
Engineering/Mechanical/Gen 3/{FOCI}{PopUp}{CameraHousing}{1}.SLDPRT
66.0 x 20.6 x 66.0 mm

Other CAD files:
Engineering/Mechanical/Gen 3/4664T420_BOLT-TOGETHER FRAMING.SLDPRT
Engineering/Mechanical/Gen 3/91090A111_ZINC-PLATED STEEL OVERSIZED FLAT WASHER.SLDPRT
Engineering/Mechanical/Gen 3/91102A755_ZINC-PLATED STEEL SPLIT LOCK WASHER.SLDPRT
Engineering/Mechanical/Gen 3/91115A133_18-8 SS FEM THRDED HEX STANDOFF.SLDPRT
Engineering/Mechanical/Gen 3/91247A599_MEDIUM-STRG GRADE 5 ZINC-PLTD STL CAP SCREW.SLDPRT
Engineering/Mechanical/Gen 3/91737A106_18-8 SS FILLISTER HEAD PHILLIPS MACHINE SCREW.SLDPRT
Engineering/Mechanical/Gen 3/92000A019_18-8 SS METRIC PAN HEAD PHIL MACHINE SCREW(1).SLDPRT
Engineering/Mechanical/Gen 3/92240A237_18-8 STAINLESS STEEL HEX HEAD CAP SCREW.SLDPRT
Engineering/Mechanical/Gen 3/92240A548_18-8 STAINLESS STEEL HEX HEAD CAP SCREW.SLDPRT
Engineering/Mechanical/Gen 3/92393A260_ALUMINUM CLEVIS PIN WITH COTTER PIN.SLDPRT
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

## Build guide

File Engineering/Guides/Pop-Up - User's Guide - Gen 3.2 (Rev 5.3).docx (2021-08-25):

# Pop-Up Buoy User’s Guide

# (Gen 3/Rev 5.3)

Table of Contents

# 1. Background

The Pop-Up Buoy was developed as a unique product designed to take measurements while sitting under sea ice in the Arctic - to fill the gap in available technology between year-round deeper moorings and surface-based sampling in the summers. Measuring just under sea ice is of particular interest because the conditions there play a critical role in shaping one of the world’s most highly productive eco-systems. However, because of the harsh and unpredictable environment of shifting and breaking ice, actually acquiring measurements close to the ice during the Winter and Spring without losing instruments has been notoriously difficult. Because of the unique conditions, it needed to be robust, inexpensive, and expendable, but sophisticated enough to acquire oceanographic-quality data.

Cost was by far the driving factor in most of the design decisions and led to some atypical outcomes, such as the independent burn wire release and stripped down sensors. Since the floats only provide 1 profile of the water column, it was desirable to keep the cost around $3,000 per float. From a program-level perspective, the extremely low cost (compared to other instruments) is what makes the instrument a viable option for collecting data.

The instruments are designed to be deployed from a research vessel during the ice-free season, where they remain anchored on the bottom for many months until the surface is completely covered in sea ice. At a designated time for each device, a timed release is triggered which allows the buoys to float upward in the water column, collecting a vertical profile of the water column, until they reach the ice. The buoys remain under the ice until they are forced out by break-up and melting, transmitting their data to shore via satellite when they do arrive at the surface.

This third generation of instruments measures temperature, Sea Surface Temperature (when drifting at surface), PAR, Depth, and fluorescence (optional). It also has GPS and Iridium modules for location and transmission.

# 2. Highlights

- Sensors: Temperature (Topside), SST (Underside Temperature), Pressure, PAR, Tilt, GPS, fluorescence (optional)
- Iridium SBD (Short Burst Data) Two-way communication
- Low Cost: ~$3,000 per unit
- Utilizes ”Arduino MEGA” development board

# 3. Specifications

## 3.1. Temperature (Topside and Underside/SST)

Sensor: US Sensor NTC Thermistor Probes

Absolute Accuracy: ±0.01°C or better

Range: -5°C to +70°C

Resolution: 0.0006°C @ -2°C

0.001°C @ 10°C
0.002°C @25°C
0.01°C @50°C

## 3.2. PAR

Sensor: Skye Instruments TAG-PARQ (Special Build)

Absolute Accuracy: ±3% or better

Range: 0 to 1000 mol/m²s

Resolution: 0.048 mol/m²s

## 3.3. Pressure

Sensors: Keller PA-4LD OEM Pressure Transmitter (http://www.keller-druck.com/picts/pdf/engl/4ld_9ld_e.pdf)

Absolute Accuracy: ±70cm (10 bar)

Range: 0 to 100m (10 bar)

Resolution: 0.3cm (10 bar)

## 3.4. Tilt

Sensor: ADXL345 3-Axis Digital Accelerometer (http://www.analog.com/media/en/technical-documentation/data-sheets/ADXL345.pdf)

Absolute Accuracy: Depends on Mounting/Calibration

Sensor is accurate for Changes as little as 1.0°

## 3.5. Power

Primary Batteries: 9V, 42Ah Alkaline Battery Pack (18 Standard D Cells)

RTC Battery: 12.5mm Lithium Coin Cell (Energizer CR1220=40mAh)

GPS Backup Battery: 12.5mm Lithium Coin Cell (Energizer CR1220=40mAh)

Sampling Current: On Bottom: 78mA for 2.5 seconds/sample

Searching for GPS: 114mA for up to 180 seconds

Sending Iridium Data: 200mA average continuous plus

500mA inrush for 20 seconds

Sleep Current: 15A

## 3.6. Data

Storage: microSD or microSDHC card: 1GB to 32GB (FAT16 or FAT32)

Sample Limit: Limited by battery power and sample intervals, not storage capacity

## 3.7. Clock

Unit: DS3234: RTC with Temperature Compensated Crystal Oscillator

Maximum Error: 1.05 minutes/year (0°C to 40°C)

1.84 minutes/year (-40°C to 85°C),

## 3.8. Release

Burn Wire Unit: SubSeaSonics TR-45

Maximum Time: 170 Days after programming

Depth Rating: 244 meters

Maximum Load: 40 lbs on Burn Wire Release Link

200 lbs on Main Release Link

Burn Wire Unit: DBV Release Cylinder

Maximum Time: 24 months after programming

Depth Rating: 2000 meters

Maximum Load: 300 lbs on Burn Wire Release Link

Burn Wire Unit: DBV Release Block

Maximum Time: 24 months after programming

Depth Rating: 2000 meters

Maximum Load: 300 lbs on Burn Wire Release Link

## 3.9. Physical Parameters

Pressure Housing: 12” Trawl Float

Depth Rating: ** pressure sensor rated to 100m or 300m is limiting factor.

Trawl Float rated to 500m, Fluorometer rated to 600m.

Net Buoyancy: ~15 lbs. (freshwater, no ballast)

~8 lbs. (freshwater, ballasted)

Length: 35.0 in (88.9 cm) from top of end cap to bottom of main release link

Weight in Air: 0.0 lbs (0.0 g)

Weight in Water: 0.0 lbs (0.0 g)

# 4. Overview

The Pop-Up Buoy has a 4 phase deployment program. Each of these phases is run sequentially. The dates and times when each phase starts and ends are based on user configuration. For more information on configuring dates and times, see Section 6.5.

## 4.1. Phase 1 – On Bottom

During Phase 1, the Pop-Up Buoy is assumed to be anchored to the bottom. The unit will simply wake up, take a sample from each sensor, and go back to sleep. The bottom sample interval is nominally 1 hour, but can be changed by the user.

## 4.2. Phase 2 – Profile

During Phase 2, the Pop-Up Buoy actively waits on the bottom until it senses a change in depth. Once the unit senses a change in depth, it will take samples from each sensor at 4 times per second, for a set amount of time (nominally 90 seconds), collecting a vertical profile of the water column on its way to the surface (or ice).

The unit is designed to wake up a significant amount of time before the scheduled release (nominally 6 hours). Since the burn wire release uses an independent clock, this ensures the unit will sense the start of the profile, regardless of any drift in either clock or minor offsets when programming either.

## 4.3. Phase 3 – Under Ice

The unit will take sample and search for a GPS location at standard interval (nominally 1 hour). As soon as the unit is able to obtain a GPS fix, it will begin attempting to transmit data via Iridium. If any messages are sent successfully, the unit will continue sending messages until all data has been sent. The unit will also only wait 5 minutes in between samples if data is sent successfully in order to transmit data back more quickly. The unit can also receive messages when it is transmitting data.

Once all data has been sent, the unit will revert into a ‘drifter’ mode, where it will sample, search for a GPS fix, and attempt to transmit its position once per day.

## 4.4. Example

The following is an example of a deployment description which is provided after programming a unit for deployment. This is from a deployment on the DY17-08 Cruise. All items in parentheses ( ) or brackets [ ] are configured by the user.

Deployment Schedule:

--PHASE 1--

Unit will start sampling [Sep 27 2017 00:00:00] and take a sample every (6h,0m,0s)

--PHASE 2--

Release Expected [Feb 20 2018 15:00:00] (<--Set Burn Wire Release for this exact time/date.)

Unit will wake up (2h,0m,0s) before scheduled release and wait for profile.

Start of profile will be triggered by a change in depth of (3 meters).

Profile will sample at 4 Hz for (0h,1m,30s) seconds before proceeding to phase 3.

If unit does not sense the release within (4h,0m,0s) of waking it will assume it missed the profile and proceed to phase 3.

--PHASE 3--

Unit will assume it is under ice until [Feb 20 2018 18:00:00]

Unit will take a sample every (1h,0m,0s) and search for GPS location only once a day to conserve battery power.

--PHASE 4--

Unit will no longer assume it is under ice after [Feb 20 2018 18:00:00]

Unit will take a sample and search for GPS location every (1h,0m,0s)

Unit will search for GPS (1 times) for (0h,2m,0s) with (0h,0m,20s) between each attempt to confirm a lock.

If unit does successfully find a GPS lock, it will attempt to send data back in the following order:

1-File Summary, 2-Profile Data, 3-Under Ice Data, 4-Bottom Data

If any messages send successfully, the unit will automatically make another attempt in (0h,5m,0s)

Otherwise, the unit will return to sampling and searching for GPS every (1h,0m,0s)

# 5. Interface

## 5.1. Arduino IDE

The Pop-Up Buoy Uses the Arduino IDE (Integrated Development Environment) to upload programs to the Buoy. The Arduino IDE is a software package that lets users write and upload code directly to the microcontroller on the device.

There are 2 different programs that must be uploaded for checking and deploying the instrument. Instructions for how to upload programs and how to configure the instrument are in subsequent sections of this guide.

Be sure to only use Version 1.8.5 of the Arduino IDE. There are difference in library packages and the way programs are compiled which may have unpredictable consequences if another version is used.

The PCB Stack must be connected to 9V power when uploading and using programs. Since power is provided through USB Cable, the unit will still communicate if not connected to power, but will circuits and sensors will not initialize properly, causing errors. Detailed instructions are provided in Section 5.3.

## 5.2. Program (Sketch) Descriptions

Pop-Up Buoy uses 3 different programs, all described below. The Arduino IDE calls these different programs ‘sketches’.

Setup and Sensor Check (PopUp_5.3_SetupAndSensorCheck.ino)

This program is used during the assembly and testing phases to test that various sensors and utilities on the units are working properly. Once uploaded and the serial monitor is launched, the user is provided a status summary of the unit and a menu to check sensors and utilities one by one. If there are any problems that require changes such as re-connecting a sensor, it is usually necessary to close the serial monitor and re-upload the program. This will allow all sensors to initialize properly.

For details and instructions on using the Setup and Sensor Check Program, see the Pop-Up Buoy User’s Guide.

Deployment (PopUp_Deployment_5.3_Arduino_1.8.5.ino)

This program is used for deployments and calibrations. All deployment parameters (dates, sample intervals, etc.) must be manually entered into the program before uploading.

Once the program is uploaded and the serial monitor is launched, the user will be provided a long dialog confirming deployment parameters and verifying unit status. This dialog should be reviewed carefully for any possible errors.

For details and instructions on configuring units for deployment, see the Pop-Up Buoy User’s Guide.

## 5.3. Uploading Programs (Sketches)

To upload different programs to the Pop-Up Buoy, follow the steps below:

1. Connect all necessary sensors, antennas, coin cell batteries, and micro SD Card to unit electronics.
2. Connect unit to Power Supply (9V Battery or Power Supply with 9V, 1A with power on). Note: Do not use the main battery packs for testing or calibrating as it will deplete power necessary for the final deployment.
3. Connect unit to computer via USB cable
4. Open the Arduino IDE (Integrated Development Environment). Be sure to use version 1.8.5.
5. Open appropriate sketch
6. Select Board
  - Tools → Board → Arduino Mega 2650 or Mega ADK
7. Select COM Port
  - Check Device Manager → Ports to find correct port
  - Tools → Serial Port → COM__
8. Compile Sketch
  - Ctrl + R or Sketch → Verify/Compile
  - Should Read “Done Compiling” when complete
9. Upload Sketch
  - Ctrl + U or File → Upload
  - Should Read “Done Uploading” when complete
10. Launch Serial Monitor
  - Ctrl + Shift + M or Tools → Serial Monitor
  - Note: The baud rate should be set to 115200 (lower right-hand corner after launching Serial Monitor)
  - Note: 9V Power MUST be supplied and turned on before the serial monitor is launched. It is possible to upload sketches without external power, but power must be supplied for sensors to initialize properly when serial monitor is launched.
11. To upload a different sketch, close the serial monitor and begin at Step 5. It is not necessary to disconnect the unit from power or close the Arduino IDE.

# 6. Preparing the Instrument for Deployment

For a proficient user, it should take about 30 minutes to check and prepare each Pop-Up buoy for deployment. This includes checking battery voltages; checking sensors; configuring sample intervals, dates, and times; installing the end cap; de-pressurizing the float; programming the burn-wire release; and arming the release for deployment.

## 6.1. Pre-Deployment Checks

- Check the main battery voltage (Should be ~9.68V)
- Check RTC and GPS coin cell battery voltages (Should be ~3.3V)
  - Touch one voltmeter probe on top of coin cell battery and the other probe to any black test point on the board
- Check that a micro SD Card is inserted
- Check that all sensors and antennas are plugged securely into electronics and wires will not get fouled or cut when installing the end cap. Be careful to observe polarity and location of the 2-pin connectors for PAR, Temperature, and Power as they are all the same size. See Section 6.1 for details.
- Ensure electronics stack is securely fastened to PCB Frame with standoffs, screws, and lock-washers
- Tape a desiccant pack to the back of the PCB Frame, also securing the electronics stack

## 6.2. Pre-Deployment Test Program

Follow the procedures in section 5.3 to upload the sketch named PopUp_SetupAndSensorCheck_4.0_12-8-17

After Launching the Serial Monitor, you will be given a status menu of options. Simply type a number into the dialog at the top of the serial monitor and press Enter to select each option. Type ‘Q’ into the dialog and press Enter to stop any of the sensor check functions.

YOU MUST SET THE CLOCK AND CLEAR THE MICRO SD CARD USING THIS PROGRAM. All other functions are a good verification that utilities and sensors are working, but are not necessary to do before deployment.

To verify that utilities and sensors are working:

1. Display Status
  - Display the SD Card status, RTC time/date, and sensor values.
  - Verify that the SD card is communicating properly and RTC is keeping time with the status function
  - If the SD card is displaying an error, try a Loopback Test (https://support.arduino.cc/hc/en-us/articles/360020366520-How-to-do-a-loopback-test).
2. Set RTC Time/Date
  - Follow the prompts to set the unit’s clock time and date. Set the clock as close to official time as possible - this way the unit’s clock can be compared to time obtained from GPS and clock drift can be accounted for.
  - ALWAYS USE UTC
3. Display SD Card Data
  - Display the contents of the SD Card. The SD Card should always be empty before deployment so that only deployment specific data is transmitted via Iridium.
4. Check Temperature Sensor
  - Display the current temperature sensor reading and the reference resistor reading.
  - The responsiveness of the temperature sensor can be checked by simply holding the probe between 2 fingers and looking for an increase in temperature.
  - The reference resistor should always read close to 10 kohms.
5. Check Pressure Sensors
  - Display the current pressure measurement value and calculated depth for both sensors.
  - The responsiveness of the sensors can be checked by covering the port with your fingertip
6. Check Accelerometer
  - Display the current accelerometer reading and approximate angle of the sensor.
  - The accelerometer should read approximately 180 degrees from vertical when the sensors are resting on the surface of a table. It should read approximately 0 degrees when the sensors are pointed upright as they are when the unit is deployed.
7. Check PAR Sensor
  - Display the current PAR sensor reading.
  - The PAR sensor should read close to 0 mol when the sensor is covered and dark. The sensor should read low values (under 10mol) when exposed to interior/artificial light. The sensor should read high values (100-1000+ mol) when exposed to outside sunlight, even if indirect.
8. Check GPS
  - Turn on the GPS module and attempt to find a GPS fix. Display processed NMEA data to the Serial Monitor.
  - The antenna must have clear view of the sky to be able to obtain a GPS fix. This does not need to be done during final checks, especially since the unit will probably be configured indoors.
9. Check Iridium
  - Turn on the Iridium module and attempt to send a message
  - The antenna must have clear view of the sky to be able to obtain a GPS fix. This does not need to be done during final checks, especially since the unit will probably be configured indoors.
X. Delete all SD Card Data
  - The SD Card should always be empty before deployment so that only deployment specific data is transmitted via Iridium.
  - If preparing for deployment and the card is not empty, enter ‘X’ at the main menu. Be careful as this does permanently delete all SD Card Data.

## 6.3. Battery and Data Calculator

Use the Battery and Data Calculator spreadsheet (Pop-Up Battery and Data Calculator - Rev 4.0.xlsx) to verify unit’s battery will last through the full deployment using desired sample intervals and cutoff times and dates. The Battery and Data Calculator also automatically calculates the time that should be programmed into the burn wire release so that it is synchronized with the Pop-Up Buoy.

See Section 4 for descriptions on the unit’s programming

To use the Battery and Data Calculator:

1. Fill in all Unit Settings which are highlighted in yellow.

Current Time: The current time and date. Be sure this time zone and the time zone of the unit’s RTC are matched. It is best to use local time to avoid errors in setting the burn wire release.

Unit Start: The time and date that the unit will take its first sample. This must be after the current time and date. Set the Unit Start for several hours or days in the future to ensure this does not lapse while programming the unit.

Release Time: The time and date that the unit will release from the bottom to collect a profile. This value and the Current Time are used to calculate the Burn Wire Programming settings which are showed in green. This value should be the exact time and date that the release is expected. The unit will automatically wake up before the release is expected and wait for the profile to begin.

Ice Free Date: The time and date that the unit is earliest expected to be free of the ice. This is primarily used as a battery saving measure. This can be set for just after the release time if there is adequate battery power or the unit may actually surface in open water.

Bottom Sample Interval: The number of seconds between samples while the unit is on the bottom. This is nominally set to 3600 (1 hour) as measurements should not change much while on the bottom.

Pre-Release WakeUp Interval: The number of seconds that the unit will wake up before the release time. This is nominally set to 7200 (2 hours) to provide a huge buffer for drift in the burn wire’s clock or small offsets when programming.

The worst case timing error for the burn wire releases is +/- 2 minutes per month, plus an additional 10 to 20 minutes for the actual erosion of the link to take place. The burn wire can also only be set in 7 or 8 minute increments. The worst case timing error for the Pop-Up Buoy’s internal clock is 1.84 minutes per year. This can cause a total worst case error of up to 40 minutes over 6 months. The Pre-Release WakeUp Interval should be set to a minimum of 3600 (1 hour). 2 Hours is probably adequate, but until the burn wire releases have been used for several seasons, some extra buffer should be added.

Under Ice Sample Interval: The number of seconds between samples after the unit has released from the bottom. This is nominally set to 3600 (1 hour) as data is more critical and variable here than on the bottom, but faster sample intervals will likely utilize too much power.

Profile Length: The number of seconds that the unit will collect a profile for after sensing a change in depth when it releases from the bottom. The profile length is nominally 90 seconds. Profile samples are collected at 4 Hz and the Pop-Up Buoy ascends at a rate of approximately 1m/s. Increasing the length of the profile will substantially increase the amount of data that needs to be transmitted because samples are collected quite rapidly. Avoid setting the profile length to longer than 2 minutes.

2. Fill in the field below (in yellow) to test check how many days the unit can stay under ice before surfacing.

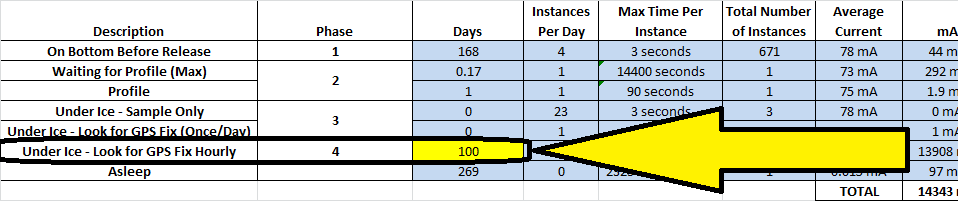
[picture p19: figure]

3. Use the graph of Battery Power and Power Estimate Table to check that the unit has enough reserve battery power to surface and send all data back. The unit should have at least 5-10% of its power in reserve, even for the worst case scenario.

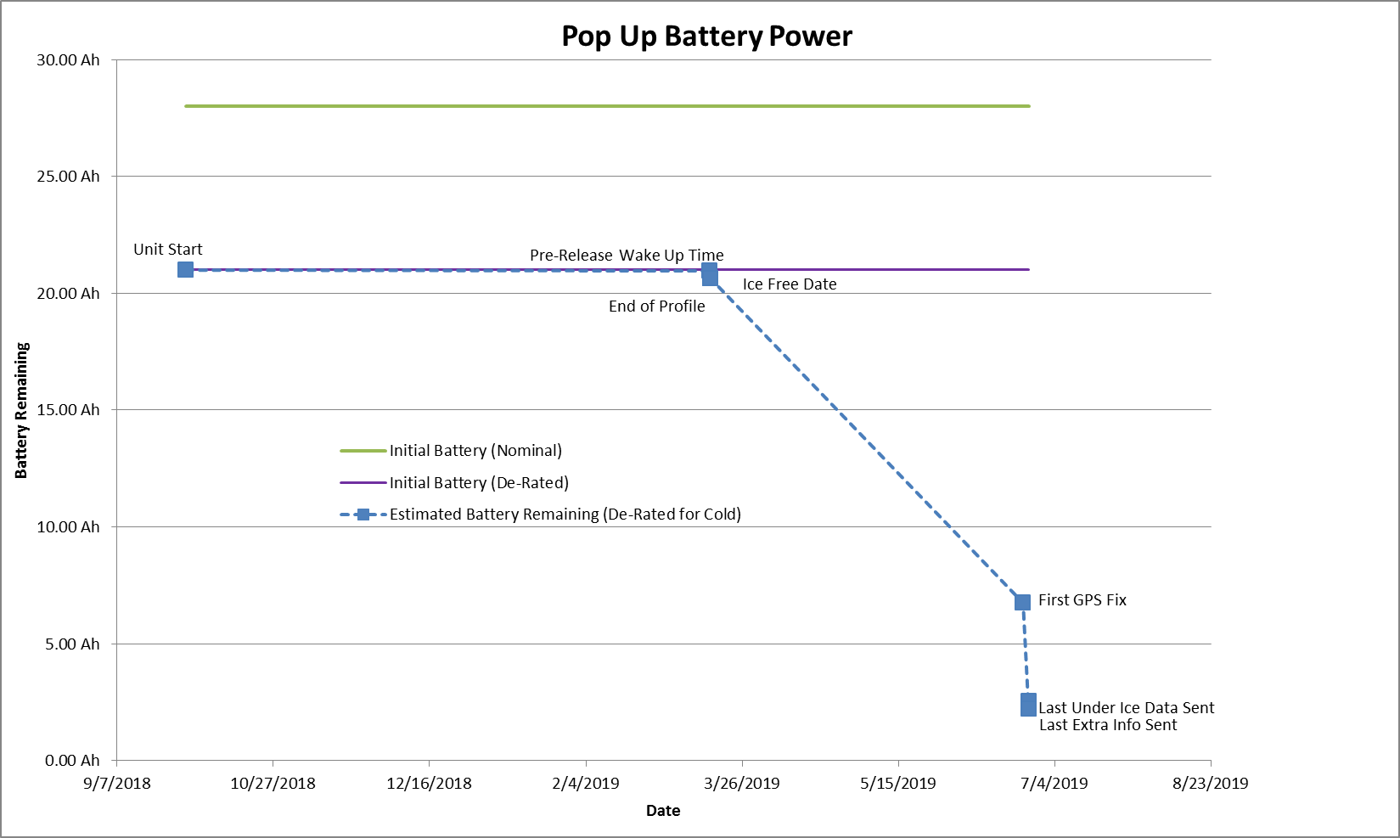
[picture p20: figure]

4. If the graph and table above do not show that the unit has adequate power reserves, change the deployment parameters to improve power usage.
  - Set the “Ice Free Date” to several weeks or months after the Release Date. This will provide the largest power savings.
  - Increase sample intervals or reduce profile length to reduce the amount of power used sampling and also reduce the amount of data that must be transmitted.

## 6.4. Final Programming of the Unit

1. Complete Pre-Deployment checks show in Sections 7.1 and 7.2.
2. Open the sketch titled PopUp_Deployment_4.0_9-17-17. Do not upload the sketch yet.
3. Setting the deployment parameters (sample intervals, release time, etc.) requires manually changing the values in the sketch. This section starts on line 57 and is clearly denoted with asterisks (***************************************************************)

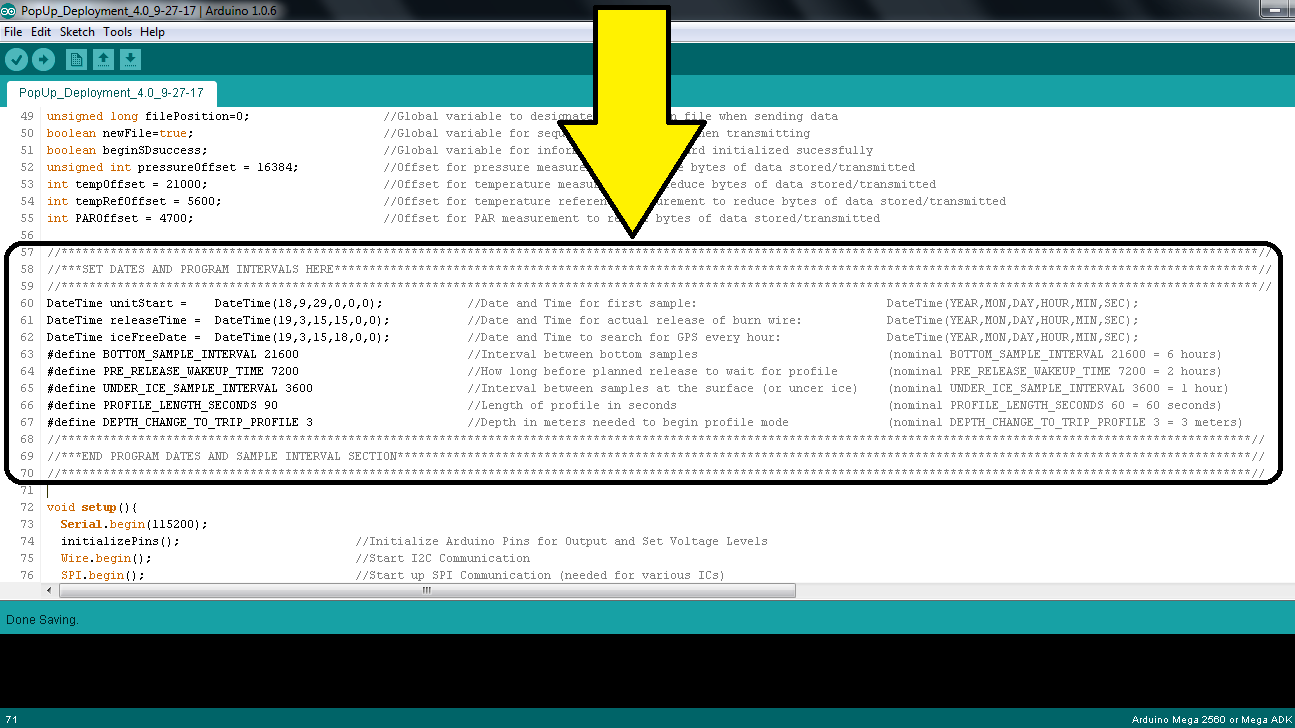
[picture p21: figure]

4. The parameters are explained below.
  - Carefully note the format of the Date Times
  - Only change the numerical values from lines 60 to 67. Making any other changes could cause the program and the entire deployment to fail. Anything after the double // in each line is a comment (in light grey) and is not processed by the program
  - Parameters should match those used in the Battery and Data Calculator.

unitStart – The time and date that the unit will take its first sample. This must be after the current time and date. Set the Unit Start for several hours or days in the future to ensure this does not lapse while programming the unit.

Format: DateTime(Year, Month ,Day ,Hour ,Min, Sec);

*Note: All values less than 10 should be a single digit. (i.e. ‘7’ not ‘07’)

*Note: Year value should be years after 2000. (i.e. ‘19’ for 2019)

releaseTime – The time and date that the unit will release from the bottom to collect a profile. This value and the Current Time are used to calculate the Burn Wire Programming settings which are showed in green. This value should be the exact time and date that the release is expected. The unit will automatically wake up before the release is expected and wait for the profile to begin.

Format: DateTime(Year, Month ,Day ,Hour ,Min, Sec);

*Note: All values less than 10 should be a single digit. (i.e. ‘7’ not ‘07’)

*Note: Year value should be years after 2000. (i.e. ‘19’ for 2019)

BOTTOM_SAMPLE_INTERVAL – The number of seconds between samples while the unit is on the bottom. This is nominally set to 21600 (6 hours) as measurements should not change much while on the bottom.

Format: xxxxx

(Any integer value up to 4,294,967,295)

PRE_RELEASE_WAKEUP_INTERVAL – The number of seconds that the unit will wake up before the release time. This is nominally set to 21600 (6 hours) to provide a huge buffer for drift in the burn wire’s clock or small offsets when programming. The worst case timing error for the burn wire releases is +/- 2 minutes per month, plus an additional 10 to 20 minutes for the actual erosion of the link to take place. The burn wire can also only be set in 7 or 8 minute increments. The worst case timing error for the Pop-Up Buoy’s internal clock is 1.84 minutes per year. This can cause a total worst case error of up to 40 minutes over 6 months. The Pre-Release WakeUp Interval should be set to a minimum of 3600 (1 hour). 2 Hours is probably adequate, but until the burn wire releases have been used for several seasons, some extra buffer should be added – hence the 6 hour nominal setting.

Format: xxxxx

(Any integer value up to 2,147,483,647)

UNDER_ICE_SAMPLE_INTERVAL – The number of seconds between samples after the unit has released from the bottom. This is nominally set to 3600 (1 hour) as data is more critical and variable here than on the bottom, but faster sample intervals will likely utilize too much power.

Format: xxxxx

(Any integer value up to 2,147,483,647)

PROFILE_LENGTH_SECONDS – The number of seconds that the unit will collect a profile for after sensing a change in depth when it releases. The profile length is nominally 60 seconds. Profile samples are collected at 4 Hz and the Pop-Up Buoy ascends at a rate of approximately 1m/s. Increasing the length of the profile will substantially increase the amount of data that needs to be transmitted because samples are collected quite rapidly. Avoid setting the profile length to longer than 2 minutes.

Format: xx

(Any integer value up to 2,147,483)

DEPTH_CHANGE _TO_TRIP_PROFILE – The change in depth (in meters) that the unit must sense to start the profile while in Phase 2. This value may be as small as 1, but should be higher depending on tidal range and the Pre-Release WakeUp Interval. If the Pre-Release WakeUp Interval is set to 6 hours, the unit will wait for a depth change for twice as long as the interval – up to 12 hours total. The DEPTH_CHANGE _TO_TRIP_PROFILE should be larger than the maximum tidal range within a 12 hour period (or double the Pre-Release WakeUp Interval). 3 or 4 meters is probably a reasonable value for most environments.

Format: xx

(Any integer value up to 100)

5. Double Check all parameters. Below is an example of how the parameters would look for the settings shown in Section 7.3.

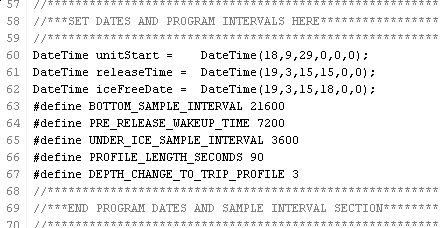
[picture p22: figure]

6. Ensure Unit is connected to 9V Power and upload the sketch as shown in Section 5.3. If preparing the instrument for final deployment, it is ok to use the main battery as the 9V source.
7. After Launching the Serial Monitor, it should display a dialog containing all details of the deployment procedure and timeline. See the example below.

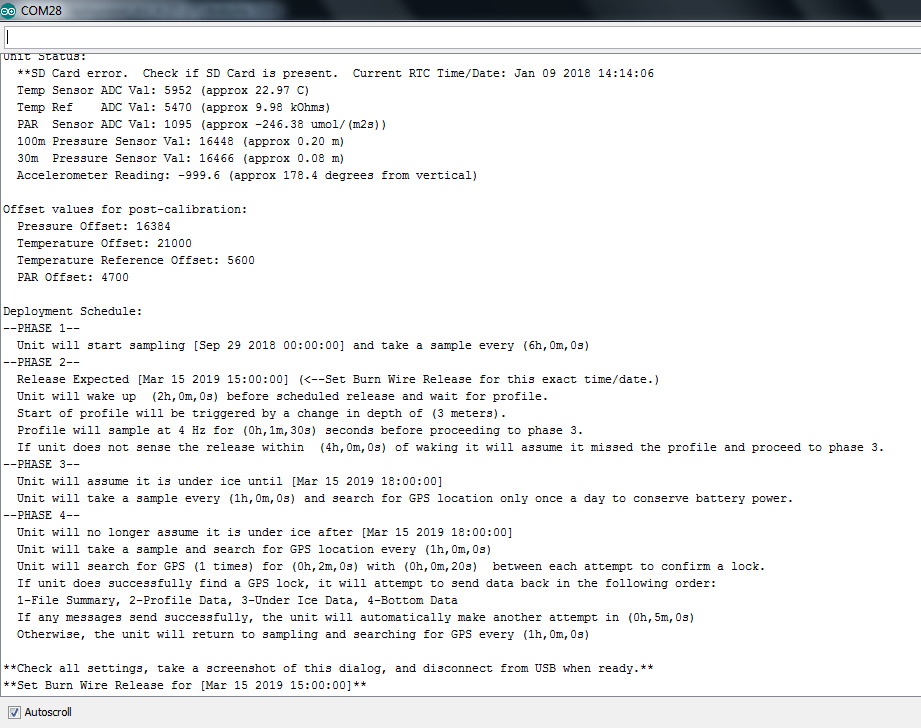
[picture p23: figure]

8. Verify all times, dates, sample intervals, and sensor functions. Be sure all details are as expected and dates and times match those in the Battery and Data Calculator spreadsheet. There are no other lights or sounds to confirm the unit has been set up properly. This window and the description are the final verification. In the example above, the first line indicates an SD Card error and the 4th line indicates an erroneous PAR reading. Both must be investigated and fixed before deploying the instrument.
9. Take a screenshot or otherwise record the dialog for record keeping. This contains important information for post-processing data and is the only record to look at if the deployment does not go as expected.
10. Write down the Burn Wire Release Time and ensure this matches what is in the Battery and Data Calculator for programming the release.
11. Once all settings have been confirmed, simply unplug the USB cable from the electronics. You are now ready to install the end cap and set the burn wire release

## 6.5. Installing the End Cap

1. Ensure the main battery is connected to the electronics in the proper position.
2. Clean and lubricate both O-rings on the end cap. Clean the mating surfaces on the trawl float.
3. Carefully insert the end cap into the float, ensuring that no wires are pinched
4. Remove the vacuum port cap with pliers if it is in place.
5. Press the end cap firmly into the trawl float until the face seal is seated against the float. Some air will be compressed inside the float when doing this. If necessary, release the extra pressure by pressing the center valve on the vacuum port with a narrow tool to get the end cap to seat fully.

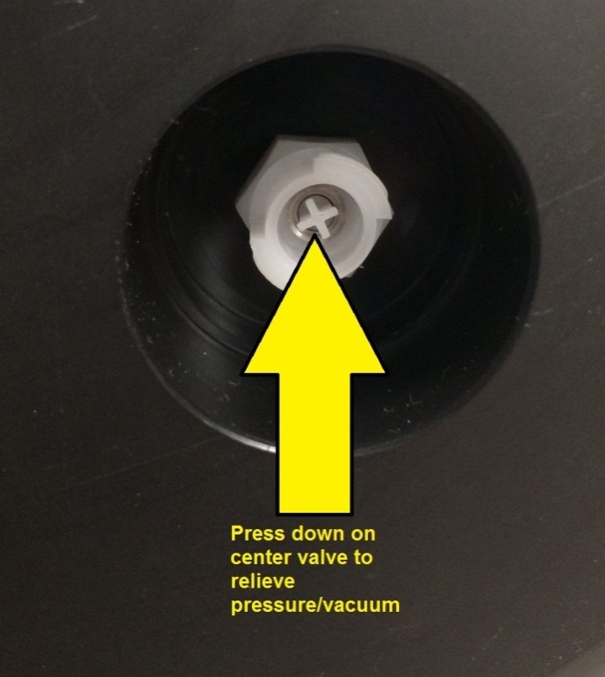
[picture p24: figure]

## 6.6. De-pressurizing the Float (pulling a vacuum)

Once the end cap is installed, air must be removed from the trawl float to create a vacuum and hold the end cap in place.

1. Connect the quick-connect tubing to the vacuum port and turn the fitting 1/4 turn clockwise to lock in the connector.
2. Pump the inside of the float to a vacuum of roughly -15psi below ambient pressure. The air can be pumped out using an electronic vacumm pump or the Mity-Vac hand pump. A vacuum of -15psi will provide ~754 lbs of force holding the cap into place. If using the hand pump, be sure that the valve near the Mity-Vac nozzle is set to Vacuum.

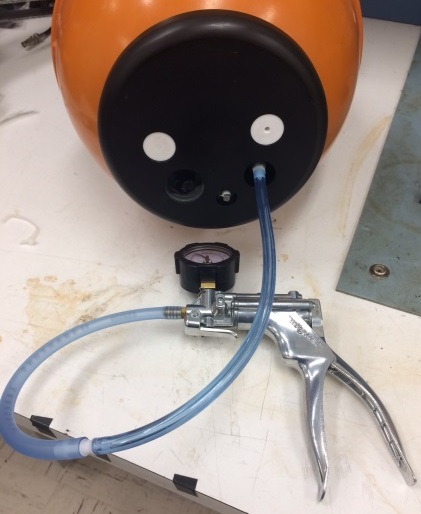
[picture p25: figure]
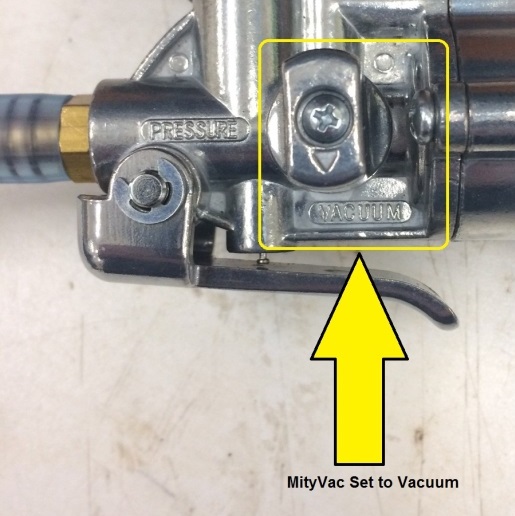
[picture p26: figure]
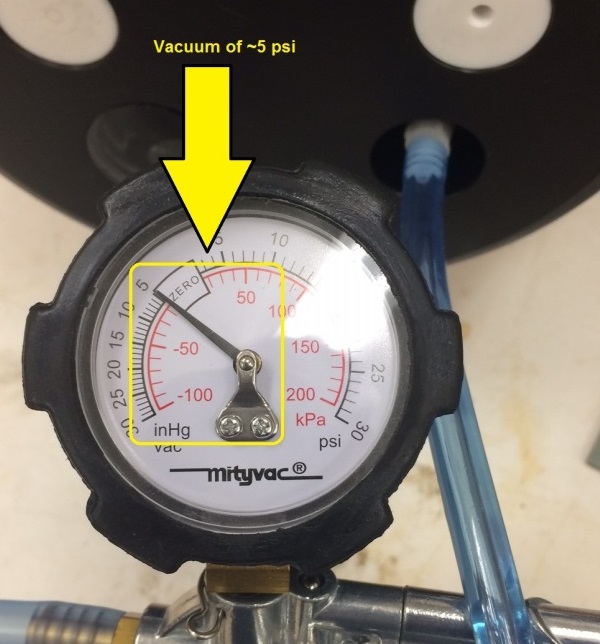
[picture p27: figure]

3. Disconnect the tubing from the vacuum port by turning the fitting 1/4 counter clockwise and removing it
4. Replace the Vacuum port Cap. The vacuum port is not watertight on its own. First, clean and lubricate the O-ring on the cap. Next, clean the mating surface on the end cap. Install the cap by pressing it firmly into the socket. Once installed, press down on the cap firmly to force the compressed air out and get it to seat as low as possible.

## 6.7. Programming the Burn-Wire Release

See document “DBV Burnwire Programming Guide-July2019”

# 7. Post-Deployment

## 7.1. Iridium Network

In 2018 - 2019 we used the DoD DITCO network contract for paying for satellite transmission of data. In order to activate these Iridium modems we had to send them to NAL Research to get “whitelisted”, a process that essentially clears devices for use on a DoD network. The contract was renegotiated and became cost-prohibitive, so we switched to using an Inmarsat Gov contract from 2020 – 2021. In order to activate the Iridium modems, you have to contact Ben Carlson and provide the modem’s IMEI number, and ask to have that number added to the Inmarsat Gov contract. Once the device is activated on the contract we keep it active until all data has been transmitted. We generally don’t deactivate and reactivate because there is a $250 charge to re-activate an existing card. Once we deactivate something, we replace it with a new one because there is no activation fee for new SIMs. The SBD monthly fee plus estimated data transmission cost per float is about $230 for a full year: broken down by $13.45 monthly rate + ($1.03/1024000 bytes transmitted x

## 7.2. Data Processing

See document \EcoFOCI_PopUp\Data\documentation\PUF Data Processing Instruction.txt

and the Background and Instruction Jupyter Notebook scripts located in \EcoFOCI_PopUp\Data\src.

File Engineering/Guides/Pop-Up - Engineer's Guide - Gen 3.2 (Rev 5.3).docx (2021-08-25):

# Pop-Up Buoy Engineer’s Guide

# (Gen 3/Rev 5.3)

Table of Contents

# 1. Background

The Pop-Up Buoy was developed as a unique product designed to take measurements while sitting under sea ice in the Arctic - to fill the gap in available technology between year-round deeper moorings and surface-based sampling in the summers. Measuring just under sea ice is of particular interest because the conditions there play a critical role in shaping one of the world’s most highly productive ecosystems. However, because of the harsh and unpredictable environment of shifting and breaking ice, actually acquiring measurements close to the ice during the winter and spring without losing instruments has been notoriously difficult. Because of the unique conditions, it needed to be robust, inexpensive, and expendable, but sophisticated enough to acquire oceanographic-quality data.

Cost was by far the driving factor in most of the design decisions and led to some atypical outcomes, such as the independent burn wire release and stripped down sensors. Since the floats only provide 1 profile of the water column, it was desirable to keep the cost around $3,000 per float. From a program-level perspective, the extremely low cost (compared to other instruments) is what makes the instrument a viable option for collecting data.

The instruments are designed to be deployed from a research vessel during the ice-free season, where they remain anchored on the bottom for many months until the surface is completely covered in sea ice. At a pre=programmed time for each device, a timed burn-wire release is triggered which allows the buoys to float upward in the water column, collecting a vertical profile of the water column, until they reach the ice. The buoys remain under the ice until they are forced out by break-up and melting, transmitting their data to shore via satellite when they do arrive at the surface.

This fourth generation of instruments measures tilt, temperature, sea surface temperature (when drifting at surface), PAR, depth, fluorescence (optional) and a low-resolution camera (optional). It also has GPS and Iridium modules for location and transmission.

# 2. Sensors

## 2.1. Fast Response Temperature Sensor

Purchased from US Sensor and TTI via part number USP19572 REV A, this has a long 23 week lead time.

## 2.2. Sea Surface Temperature Sensor

Made in-house with SS316 size 3 SAE ORB pipe plug purchased from Titan Fittings. 50Kohm thermistor potted in Arctic Silver alumina, soldered to silicone 22AWG lead wires.

## 2.3. PAR Sensor

The PAR sensor used on the Pop-Up buoys is a TAG-PARQ by Skye Instruments. This is the same sensor as used on the initial prototype of the Pop-Up Buoys and integrated into the satellite tag provided by the University of St. Andrews. It was shown to have excellent response, even in very low light conditions.

The TAG-PARQ sensor costs only $340 whereas the least expensive alternative (a LICOR PAR sensor) is around $800.

One tradeoff for this sensor is that the TAG-PARQ is a simple photodiode with an analog output in As. An amplifier circuit is built into the main electronics to properly amplify and convert the signal.

A second tradeoff for the TAG-PARQ sensor is that it is not waterproof and must be installed in a separate housing. Ideally, this should be a perfect cosine diffuser so the angle of incident light does not affect the signal. The acrylic housing used in the Pop-Up buoys is not a perfect cosine diffuser, but works well within the 3% margin of error the sensors are calibrated for. Testing showed the acrylic absorption by acrylic can be easily corrected for with a calibration factor, multiplying the measured signal by 1.15.

The graphs below show an example of how the PAR sensors perform compared to a commercial instrument in low light conditions and in response to changing the incident angle of light.

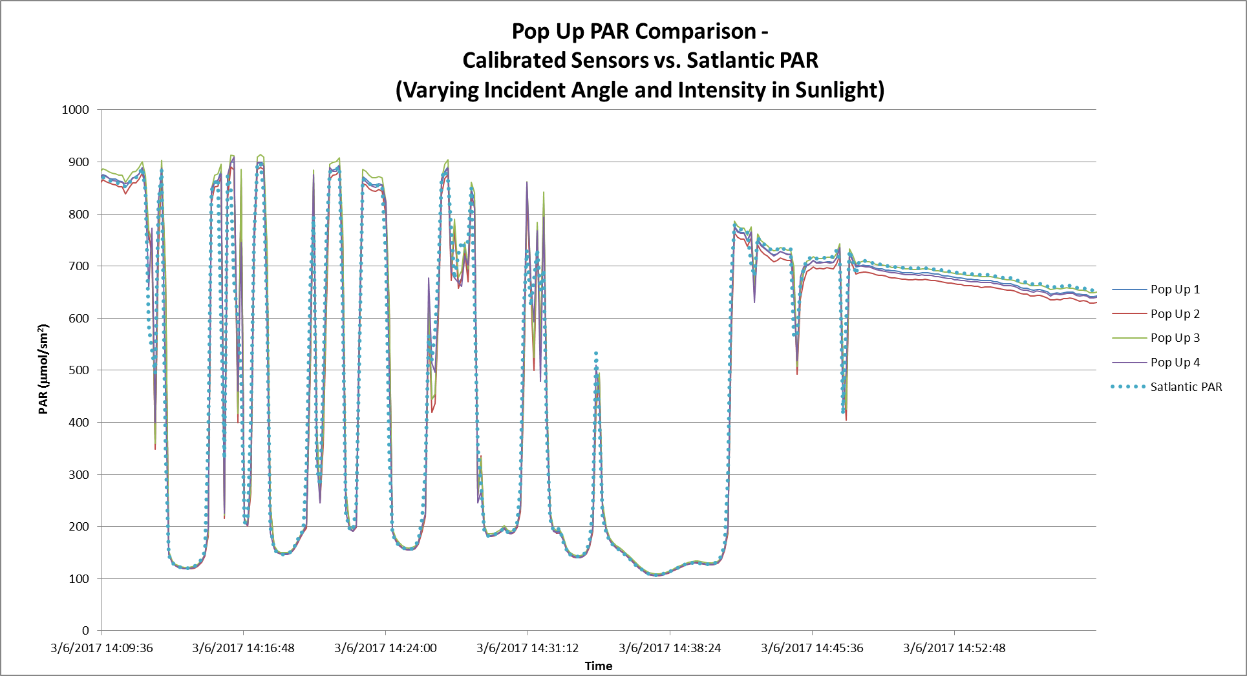
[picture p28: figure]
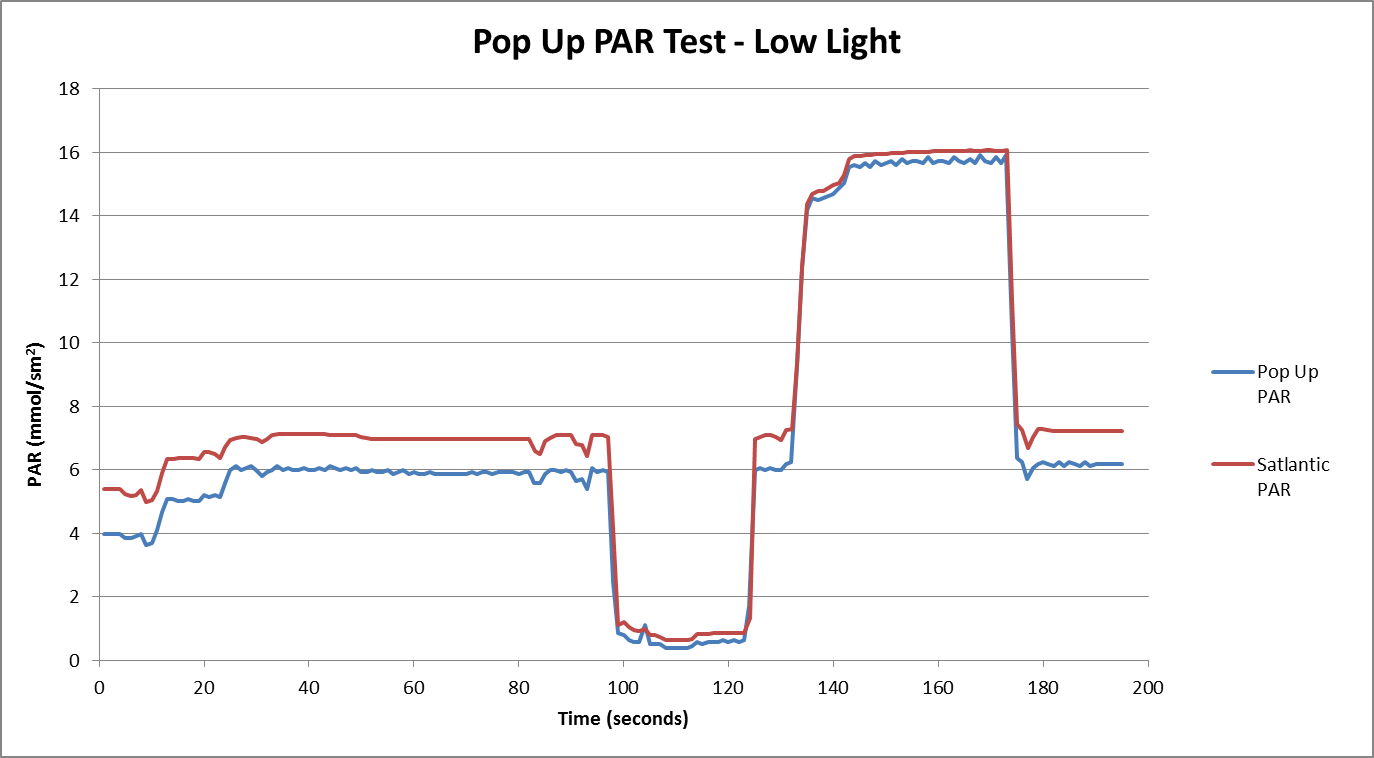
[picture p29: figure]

## 2.4. Pressure Sensor

The Pop-Up Buoys have a Keller PA-4LD OEM Pressure Transmitter (http://www.keller-druck.com/picts/pdf/engl/4ld_9ld_e.pdf) with embedded signal conditioning that measures pressure. It outputs digital data using I²C communication and does not require any calibration. It is a very accurate sensor (0.7% FS) for a cost of only ~$120 each. These are the same sensors used on PMEL’s Prawler, so both the housing and small attachment PCB were taken directly from Prawler designs.

## 2.5. Fluorometer

Turner Cyclops 7F Fluorometer

## 2.6. Camera

4D U-Cam III micro-cam. Low resolution, low power.

## 2.7. GPS

The GPS Chosen for the Pop-Up buoys is a low power, low cost GPS Module. It is the same module used on Adafruit’s Ultimate GPS Breakout (https://learn.adafruit.com/adafruit-ultimate-gps/overview). This made it an easy choice for prototyping and rapid development, but the module also has excellent sensitivity, time-to-fix, and power requirements – all at low cost. The modules can be purchased from 3rd party sellers such as Adafruit, but are less expensive if purchased directly from the manufacturer.

## 2.8. Iridium Module

The Iridium Module used in the Pop-Up buoys is a RockBLOCK 9603 (https://www.rock7mobile.com/products-rockblock.php). This device is a very low cost SBD (Short Burst Data) Iridium module. Once again, cost was the main driver for choosing this module as they cost only approximately $250 each. Additionally, the modules were made to interface quickly and easily with controllers such as the Arduino boards and can be powered with only 5V DC. A very thorough IridiumSBD library (http://arduiniana.org/libraries/iridiumsbd/) was also developed specifically for using the RockBLOCK with an Arduino board, which also facilitated prototyping. Note: Some minor, but critical modifications were made to the IridiumSBD library for the Pop-Up buoys – refer to section 4.2.1 for more details.

The RockBLOCK 9603 allows for 2-way communication with the Pop-Up Buoys. Once the buoys surface, users are able to send commands to re-send any data that is lost or to adjust the interval of position updates once all data has finished sending. Currently 2-way communication has not been integrated into the Arduino code, but may be a future project direction.

### 2.8.1. SBDIX Key

The SBDIX command denotes the status of your sent, received and queued messages:

<MO status> - Any returned number with a value of 0 to 2 indicates your message has been successfully transmitted. Any number above 2 indicates that the message has not been successfully transmitted.

<MOMSN> - This number denotes the MO message number and cycles between 0 and 65535.

<MT status>
0 - No messages waiting to be received.
1 - New message successfully received.
2 - Error during mailbox check / message reception.

<MTMSN> - This number denotes the MT message number and cycles between 0 and 65535.

<MT length> - The size (in bytes) of the MT message.

<MT queued> - The number of MT messages in the queue waiting to be downloaded.

# 3. Mechanical Design

## 3.1. Trawl Float

12” Trawl floats are used for the Pop-Up Buoy’s main housing because they are very inexpensive, machine well, and the shape is ideal for under the ice. The round and robust housing is designed to ‘ride’ under the ice, where traditional instruments are easily destroyed. The trawl floats cost only around $35 and are nominally rated for a depth of 600 fathoms (1097meters).

## 3.2. End Cap

The end cap design is used to consolidate all electronics and sensors into a single package and protect the instrument’s sensors and antennas. Once the electronics package and sensors are assembled together in the end cap, it can be easily assembled or removed as needed for testing and deployment.

All sensors are either flush with the upper surface of the end cap or slightly below to protect them from damage under the ice. This is critical for this instrument. Additionally, the GPS and Iridium antennas are actually mounted under the end cap, further protecting them. These antennas on other instruments are typically very vulnerable to damage or icing, leading to instrument failure. The interference from the end cap does attenuate and distort the communication slightly, but the cap is thin enough that both GPS and Iridium work effectively.

The End Cap has 2 o-ring seals for extra security: One face seal and one piston seal. The trawl floats are too thin to place two piston seals on the cap. The end cap is a half-dovetail groove because the o-ring is in between sizes and the dovetail is needed to hold the o-ring in place while assembling.

A vacuum port is placed in the end cap which is used to pump air out of the float once sealed. This creates a vacuum inside the float and holds the end cap on firmly. A vacuum of ~10psi provides ~300 lbs of force holding the cap down. There is a pressure relief valve on the center of the valve which should be used to relieve pressure when disassembling the float.

## 3.3. Frame

The frame is made from zinc plated steel strapping purchased from McMaster-Carr and bolted to the trawl float lugs, making use of three rubber spacers and oversized washers to hold the frame away from the float body. The frame is bolted between the lugs and the release mounting block (we used a steel brick for Gen 3.1, and purple heartwood for Gen 3.2).

# 4. Electronics

### 4.1.1. Arduino MEGA

The Arduino MEGA was used in the design of this instrument primarily to simplify the design process (that and the principal engineer was not formally trained in electronics, thus had to make some accessions). The Arduino platform is an open-source development platform, which combines a micro-processor, some fundamental software libraries, and a programming environment to make it very easy for newcomers to develop electronics equipment. Since the Arduino is open-source, there are volumes of information online about the specifics which will not be discussed here. The Arduino MEGA is one of many Arduino boards and was chosen because a) it has more input/output pins necessary to control the various signals for this instrument and b) it has extra hardware Serial ports, which are required for the Iridium module.

One main drawback of using the Arduino platform is power consumption. When the Pop-Up Buoy is just sampling sensors, it draws ~80mA. Other simple oceanographic instruments often draw less than 10 mA. This is still tolerable, because the instrument only needs to be on for a short time before going back to sleep. Also, the amount of power required to search for GPS and power the Iridium module while sending messages accounts for the majority of the required power budget and would be necessary regardless of what micro-controller were used.

One other major consideration must be made because the Arduino MEGA also does not have a ‘low-power’ mode. In order to overcome this problem, the Arduino is completely shut down when not sampling. As the Arduino cannot ‘wake itself up’, a RTC with a built in alarm is used to send a signal to a power converter and wake the unit. This is not a traditional or even optimal design, but it does work for the application, keeps cost down, and has proven a reliable method in several other projects (MTR-Duino and TAPS Controller).

In the future, it may be desirable to switch the design to a standard processor used for oceanographic instruments. This would have a few main advantages – a) lower power consumption when sampling, b) smoother communication with terminal programs (Arduinos can be a bit finicky), and c) a more standardized instrument which doesn’t require unique software or equipment. PMEL’s EDD should be consulted or included if choosing to pursue this approach in order to optimize and standardize the equipment as best as possible.

### 4.1.2. RTC

The Pop-Up Buoy uses a DS3234 RTC with an internal alarm to ‘wake up’ the unit from sleep at prescribed sample intervals. This is done because the Arduino does not have an on-board clock to do so and must be shut down to conserve power. The alarm is set within the program using the appropriate registers according to the DS3234 datasheet. The Shutdown pin on the LT1129 allows the Arduino MEGA to be completely shut off and then woken with a signal from the RTC.

### 4.1.3. Batteries

Standard D-Cell Alkaline Batteries are used for the Pop-Up Buoy, primarily to reduce cost. The additional weight of the alkaline batteries at the bottom of the trawl float is advantageous as it helps to keep the unit upright. The primary voltage regulator requires a minimum 5.5V input, so a 9V pack is used to allow for both de-rating for temperature effects and voltage drop as the battery is drained.

The majority of power is consumed when the unit is on the surface, searching for GPS and sending Iridium messages. See power budget spreadsheet for calculations and programming description for more on power-saving measures.

Battery packs can be obtained from A-Pak batteries (425-820-2272). The first packs cost only ~$100 each.

### 4.1.4. Temperature Circuit

The temperature circuit used in this design was adapted from the original MTR (Miniature Temperature Recorder) designed by PMEL. The original MTR used a circuit with a shunt regulator and operational amplifier connected to the thermistor, which produced a voltage sent to a voltage-to-frequency converter, which was finally counted by the micro-processor. In the years since the original design, electronics have seen some marked advances in many areas – one of them being with Analog to Digital Converters. The ADS1100 ADC used in the Pop-Up Buoy is a self-calibrating ADC capable with 0.02% accuracy. This is just slightly less than the 0.01% accuracy needed to achieve the 0.01°C design requirement, so a 0.01%, 0.2ppm reference resistor is used not only to track any drift in the sensor, but also to correct for any inaccuracy in the ADC.

# 5. Circuit Description

## 5.1. Arduino Mega

The brain of the Pop-Up Buoy Controller is an Arduino MEGA 2650 (https://www.arduino.cc/en/Main/arduinoBoardMega2560) which controls read and write functions to various ICs, collects and stores sensor data, and communicates with the GPS and Iridium Modules. It uses I²C and SPI communications as well as digital signals for ICs and sensors, and two hardware serial lines for GPS and Iridium communications.

## 5.2. Power Regulation

Power is regulated and switched on and off with an LT1129 Micro-power Low Dropout Regulator with Shutdown (http://cds.linear.com/docs/en/datasheet/112935ff.pdf) (U21). The LT1129 provides 5V power to the board and only consumes in shutdown mode (when unit is sleeping between samples).

Both the RTC and Arduino MEGA are connected to the Enable pin on the LT1129. When waking up, the RTC alarm pulls the Shutdown signal high, turning on power to the unit. The Arduino Micro then sends a high signal via the ‘Shutdown’ Pin which keeps the unit running while the alarm is reset and sampling is completed. Eventually, the Arduino Micro sends a low voltage signal via the ‘Shutdown’ pin, forcing the Enable signal low and shutting off power to the unit. R26 is a pull down resistor to ensure the Enable signal is normally low.

3.3V power is needed for the RTC, microSD Card, Accelerometer, and I²C communication with the ADCs and is provided by U18, an LP5907 Ultra-Low Quiescent Current LDO (http://www.ti.com/lit/ds/symlink/lp5907.pdf). The Arduino MEGA does contain an onboard 3.3V regulator, but is bypassed to prevent drawing too much current through the Arduino and destroying the board.

Several AO3407A P-Channel MOSFET Transistors (http://www.aosmd.com/pdfs/datasheet/AO3407A.pdf) are used to toggle power to the 5V sensors (Q5), 3.3V Sensors (Q4), GPS (Q6), and Iridium module (Q3), in order to minimize power consumption. Pullup resistors (R19, R20, R22, and R24) ensure the input signal is normally high (power off) and a low voltage signal from the Arduino MEGA turns power on to each when needed. Current limiting resistors R17, R18, R21, and R23 are used for the digital signals to reduce current consumption flowing from the Arduino MEGA and avoid exceeding its maximum.

Additional power-regulator was added in 2019 by Dirk Tagawa:

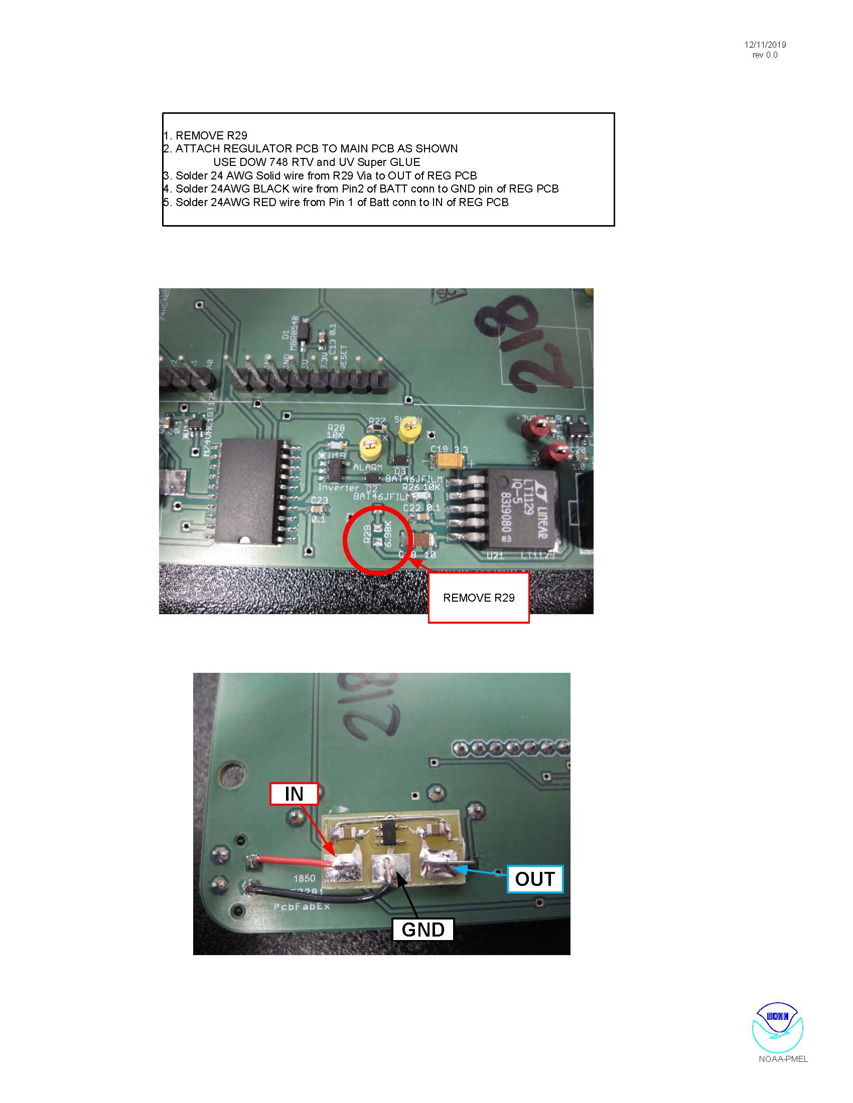
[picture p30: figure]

## 5.3. MicroSD Card, Accelerometer, and RTC

The microSD Card, Accelerometer, and RTC require SPI communications at 3.3V and the Arduino MEGA operates at 5V. U15, a MC74VHC1GT125 Non-Inverting Hex Buffer (http://www.ti.com/lit/ds/symlink/cd74hc4049.pdf) which accepts over voltage inputs, is used to lower voltages coming from the Arduino (SCK, MOSI, CS) and U14, a NC7S14 Single Non-Inverting CMOS Logic Level Shifter (http://www.onsemi.com/pub_link/Collateral/MC74VHC1GT125-D.PDF), is used to raise the MISO signal going to the Arduino MEGA.

U15 is a standard microSD Card Push-Push Socket (http://www.molex.com/pdm_docs/sd/473340001_sd.pdf) to allow the user to remove the card and download data quickly for testing and calibration, or if a unit is ever recovered.

U17 is an ADXL345 3-Axis Digital Accelerometer (http://www.analog.com/media/en/technical-documentation/data-sheets/ADXL345.pdf). Its high resolution enables measurement of inclination changes less than 1.0° and is used to measure the angle of the Pop-Up Buoy from vertical. U10, a SN74LVC1G32 Single 2-Input Positive OR Gate (http://www.ti.com/lit/ds/symlink/sn74lvc1g32.pdf), is recommended for the ADXL345 to prevent bus traffic from accidentally appearing as an I²C start command.

U20 is a DS3234 Extremely Accurate Temperature Compensated RTC (http://datasheets.maximintegrated.com/en/ds/DS3234.pdf) which provides both timekeeping function and an alarm to wake the unit up and collect samples at the proper time. B2, a 12mm lithium coin cell battery, powers the RTC when the unit’s primary power is off. U19, an NC7S14 High Speed Inverter with Schmitt Trigger Input (https://www.fairchildsemi.com/datasheets/NC/NC7S14.pdf), is used to invert the signal coming from the RTC alarm to be the proper voltage for the Shutdown input of the primary voltage regulator, U21.

When the alarm function on the RTC is not active, the INT/SQW pin is held at high impedance. This keeps the input signal to U19 at high voltage, and the output to the Enable pin low (power off). R28 is a pullup resistor to ensure the input signal to U3 is normally high. R29 is a voltage dividing resistor to keep the high side of R28 at an acceptable level for U19. When the alarm function is triggered, the INT/SQW pin on the RTC drops to low impedance, allowing current to flow and driving the input of U3 to low voltage. This causes the output of U19 to be high voltage and the high signal sent to the Shutdown pin turns power to the unit on. U19 and R28/R29 are tied to the primary battery, rather than to the coin cell, to prevent the coin cell battery from draining if the alarm is triggered, but the primary battery is dead or not connected. After all, the alarm function is only needed if the primary battery is available.

D2 and D3 are Schottky Diodes that ensure the shutdown signal coming from the Arduino and shutdown signal coming from U19 do not cause a short. The low forward voltage of the Schottky (450 mV) keeps the voltage at the Shutdown pin at the highest possible voltage to ensure the primary voltage regulator trips on.

## 5.4. Temperature Measurement

The voltage measurement for temperature is done by U6, an ADS1100 Self-Calibrating 16-Bit ADC (http://www.ti.com/lit/ds/symlink/ads1100.pdf), which achieves approximately 0.02% absolute accuracy using the settings in this instrument. The ADC requires a highly accurate power source, provided by U4, a MAX6126 Ultra-High-Precision Voltage Reference (http://datasheets.maximintegrated.com/en/ds/MAX6126.pdf).

The ADC requires I²C communications at ~3V and the Arduino Micro operates at 5V. Q1, Q2, and R5, R7, R9, and R11 are used provide bi-directional I²C communications at the proper voltages. The I²C communications are tied to 3.3V rather than 3V to keep the ADC on an isolated circuit and because the ADC/communication protocol can tolerate the small difference in voltage.

The analog portion of the circuit was adapted from the original MTRs (Miniature Temperature Recorders) designed at PMEL. It provides an almost perfectly linear voltage output between 0.05V and 1.05V when the thermistor is between -5°C (~42k) and +60°C (~2k). The non-linear portion is only at higher temperatures where higher accuracy is not normally needed in oceanographic applications. (See the LTSpice model for more specific info). After the voltage signal is output by an LT1013 Precision Operational Amplifier (http://www.ti.com/lit/ds/symlink/lt1013.pdf), a gain of 2 is applied internally by the ADC before sending the digital signal to the Arduino Micro. During calibration, the voltage measurement is directly fit to a Steinhart-hart equation, so conversion to resistance or any other values is not needed.

A 0.1°C interchangeable NTC thermistor is used, which can provide 0.1°C accuracy by using calibration coefficients from a different unit. This is advantageous if calibration is not possible for some reason, or calibration info is lost or corrupted. On the Printed Circuit Board, the analog circuit elements are on a separate isolated ground plane, linked to the main ground plane only by one small trace. This is done to reduce any potential ground noise from digital signals in the rest of the circuit.

Since 0.01°C accuracy was needed for this application, but the ADC and voltage reference can only provide ~0.02°C accuracy (~0.02%), R12, an ultra-high precision reference resistor with 0.01% tolerance and ±0.2ppm temperature coefficient, is used to correct for any inaccuracy. U7, an ADG836 Dual SPDT Switch (http://www.analog.com/media/en/technical-documentation/data-sheets/ADG836L.pdf), is used to swap out the thermistor and reference resistor in order to take the alternate measurement. Low on-state resistance and tight channel-to-channel matching make this switch optimal for providing consistent measurements. The resistors are swapped out by a single digital signal sent from the Arduino Micro which is translated to 3.3V by U5, a NL17SZ07 Single Non-Inverting Buffer with Open Drain Output (http://www.onsemi.com/pub_link/Collateral/NL17SZ07-D.PDF). R10 is a pullup resistor to make sure the output voltage is normally high and does not float.

## 5.5. PAR Measurement

The voltage measurement for the PAR sensor is done by U2, another ADS1100 Self-Calibrating 16-Bit ADC (http://www.ti.com/lit/ds/symlink/ads1100.pdf). This ADC is on an isolated, highly accurate power source – U1, also a MAX6126 Ultra-High-Precision Voltage Reference (http://datasheets.maximintegrated.com/en/ds/MAX6126.pdf). Both ADS1100 ADCs are tied to the same I²C bus and are identified by unique addresses (determined by unique part numbers when purchasing).

The analog portion of the PAR circuit is a trans-impedance amplifier, designed following the example in TI Designs TIDU535 Verified Design (http://www.ti.com/lit/ug/tidu535/tidu535.pdf)

The TAG-PARQ sensor is a simple photodiode, which outputs a small but precise current when light at the proper frequency strikes the face of the sensor. R2 and R3 form a voltage divider, biasing the non-inverting input of the op amp at 0.5V. The op amp, U3, is an ISL 28134 Ultra Low Noise, Zero Drift Rail-to Rail Precision Op Amp (http://www.intersil.com/content/dam/Intersil/documents/isl2/isl28134.pdf) – the 15nV°/C offset drift for this sensor is critical in order to not affect the small signal that is output by the TAG-PARQ sensor. Biasing the non-inverting input at 0.5V is also important to account for the maximum initial offset voltage of the op amp. R1 sets the gain of the circuit at 137,000 – providing a nominal 0.5V to 2.5V signal at the input of the ADC for PAR values of 0 to 1000 molm⁻²s⁻¹.

See the ‘PAR Circuit Calculations’ spreadsheet and the LT Spice model for more specific information.

## 5.6. Pressure Measurement

The Pop-Up Buoys have a Keller PA-4LD OEM Pressure Transmitters with embedded signal conditioning that measures pressure. The pressure sensor is connected to the same I²C bus as the ADCs and simply provide a digital value for pressure to the Arduino MEGA.

When obtained from the manufacturer, these pressure transmitters have identical I²C addresses and one must be altered to avoid communication problems. Information on how this is done is contained in the Communication Protocol document (http://www.keller-druck2.ch/swupdate/InstallerD-LineAddressManager/manual/Communication_Protocol_4LD-9LD_en.pdf) and explained in Section 6.1.

## 5.7. GPS

GPS acquisition is done by U9, a GlobalTop Technology FGPMMOPA6H Standalone GPS Module (https://cdn-shop.adafruit.com/datasheets/GlobalTop-FGPMMOPA6H-Datasheet-V0A.pdf). As soon as power to the module is switched on, it begins searching for a GPS signal and outputs serial data as NMEA output sentences, which is parsed and processed by the Arduino MEGA. Since the GPS module operates at 3.3V and the Arduino MEGA operates at 5V, U8, a NC7S14 Single Non-Inverting CMOS Logic Level Shifter (http://www.onsemi.com/pub_link/Collateral/MC74VHC1GT125-D.PDF), and U11, a TX and RX 3.3V to 5V – U8 and U11, a NL17SZ07 Single Non-Inverting Buffer with Open Drain Output (http://www.onsemi.com/pub_link/Collateral/NL17SZ07-D.PDF) are used to translate the serial data to the appropriate voltages.

B1, a 12mm lithium coin cell battery provides backup power to the GPS, which allows the unit to retain memory of previous satellite information and acquire a position lock more quickly.

The GPS unit also uses a 28dB Active External Antenna (https://www.adafruit.com/products/960) which is embedded in the end cap and connected to the SMA connector, J5.

## 5.8. Iridium Module (RockBLOCK Mk2)

Iridium communications are completed by an external RockBLOCK Mk2 (https://www.rock7mobile.com/products-rockblock.php) module which is mounted to the main board. The iridium module communicates with the Arduino MEGA using one of the MEGA’s hardware serial ports. Apart from power and serial communications, the only other connection needed for the RockBLOCK is a digital signal to the unit’s On/Off pin which is used to toggle whether it is awake or asleep. A current limiting resistor, R25, is used for the signal to reduce current consumption flowing from the Arduino MEGA and avoid exceeding its maximum.

# 6. Construction and Assembly

## 6.1. Fast Response (Topside) Temperature Sensor

These temperature probes are a custom design that were originally purchased from U.S. Sensor. U.S. Sensor was bought out by Littlefuse, Inc. and they contract out custom builds to third party companies. The company that Littlefuse contracts our part out to is TTI, Inc. Our part# for this probe is USP19572. The probe is a negative temperature coefficient (NTC) 50kOhm thermistor (https://www.princeton.edu/~cavalab/tutorials/public/Thermocouples.pdf) at 25 degrees C with +/- 1% tolerance on the resistance value. An NTC thermistor decreases its resistance with an increase in temperature, and increases its resistance with a decrease in temperature.

These probes have a 6 month lead time and should be ordered first thing, or as soon as you have a general idea of how many pop up units are being built. Always include spares in your order!

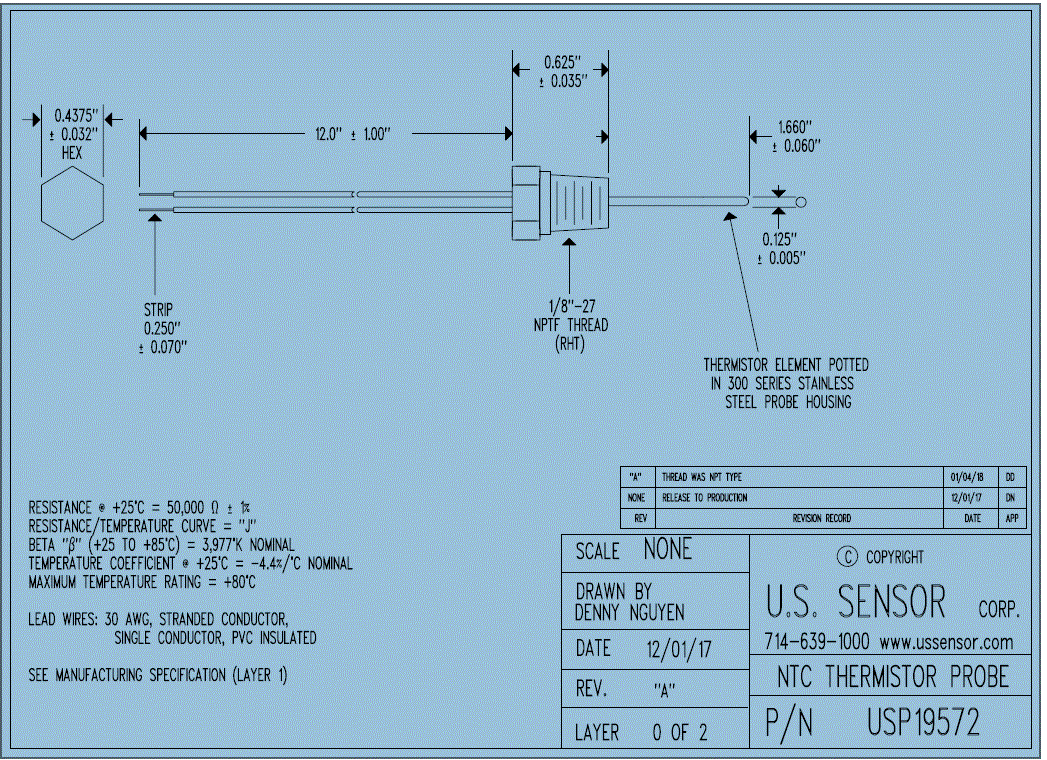
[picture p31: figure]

1. Connect Micro-Fit receptacle to wires using CONN SOCKET 20-24AWG CRIMP GOLD (https://www.digikey.com/product-detail/en/molex/0430300002/WM1125CT-ND/467811)

## 6.2. Slow Response (Sea Surface) Temperature Sensor

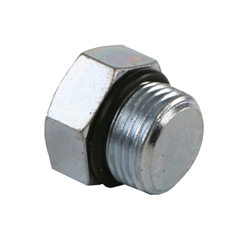
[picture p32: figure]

SAE O-ring boss (ORB) Hex Head Plug, size 3.

1. Have machine shop drill out cavity to pot thermistor into

2. Pot 50kOhm thermistor with arctic silver alumina in plug pit

## 6.3. PAR Sensor

1. Have the machine shop machine acrylic housing per specifications according to the TAGPARQ Acrylic Housing SolidWorks part and drawing files.
2. Set PAR sensor into housing on a flat working surface with leads facing upwards. Make sure the housing lens inside is clean!
3. Set the PAR sensor into the acrylic housing to protect the white photo-sensitive face of the PAR sensor as you solder.
4. Solder 12-14” of 24-26AWG wire onto the two sensor leads. Be careful to observe polarity and connect the cathode (-) of the PAR sensor to the black wire. The anode(+) is marked by a yellow triangle, connect the anode(+) to the red wire.
5. Use heat shrink to insulate the leads from each other after soldering the wires.
6. Connect Micro-Fit receptacle to wires. The hole drilled for the PAR sensor wires is large enough for the receptacle to fit through. The black wire should be in circuit position 1, indicated by a bar-like plastic ridge.

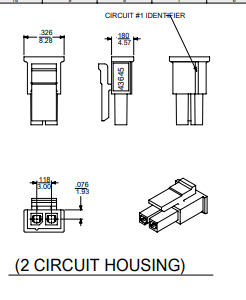
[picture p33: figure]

7. BEFORE SETTING SENSOR INTO HOUSING WITH EPOXY CONNECT SENSOR TO THE ARDUINO-CONTROLLED MAIN CIRCUIT BOARD AND TEST ADC RESPONSE. If sensor is giving ADC values that increase with increased light, continue. If not, re-do solder connections and try again.
8. Glue PAR Sensor into place using 2 part quick set Loctite epoxy. Run a very small bead of epoxy around the circumference of the PAR sensor and reset it into the housing. Let set for 5 mins. This will ensure no epoxy will leak down onto the white photo-sensitive portion of the sensor.

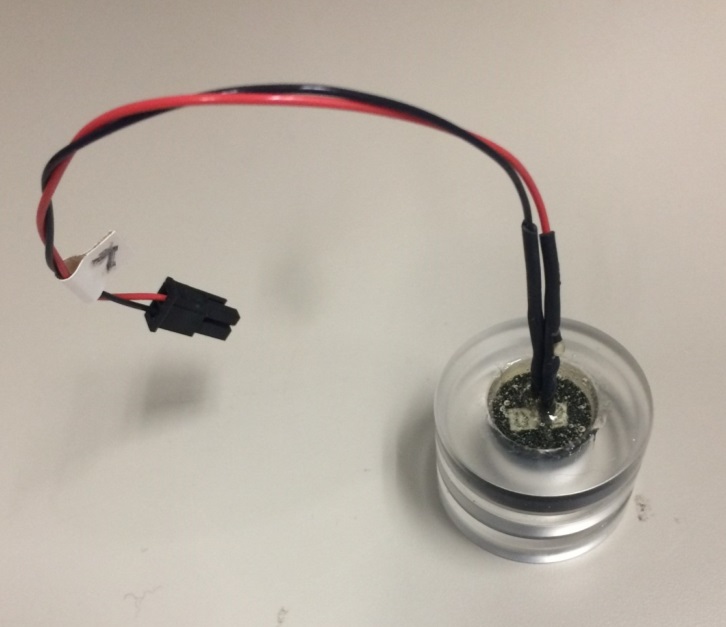
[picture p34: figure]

10. After epoxy has fully set, Clean O-ring grooves and install O-rings with a small amount of grease.
11. When removing PAR sensor from the endcap, use an awl or similar tool (pencil, eraser end) to push the edge of the acrylic housing out of the end cap from the bottom.

## 6.4. Pressure Sensor

1. Machine pressure housing per specifications.
2. Order small pressure sensor PCBs, or get spare PCBs from Prawler parts. The pressure sensor and housing is the exact same as used on the Prawler. (Keller 4-LD)
3. Mount pressure sensor into housing using a small amount of grease on the O-ring.
4. Mount pressure sensor PCB onto back of housing using screws.
5. Make sure the PCB is flush with the sensor.
6. Screw threaded hand-pump fitting into top of housing, pressurize to 5-10psi to ensure the sensor is flat against the PCB.
7. Solder leads from pressure sensor onto PCB. Remove threaded hand-pump fitting after completing this step.
8. Solder 6-8” 24-26 AWG wires to PCB. The sensor uses a simple 4 wire connection to the main Pop-Up board, with no resistors or other components needed. The 4 wires and pin-outs are shown below. This information is also shown on the pressure sensor data sheet. Wire colors have been preserved to avoid any confusion.

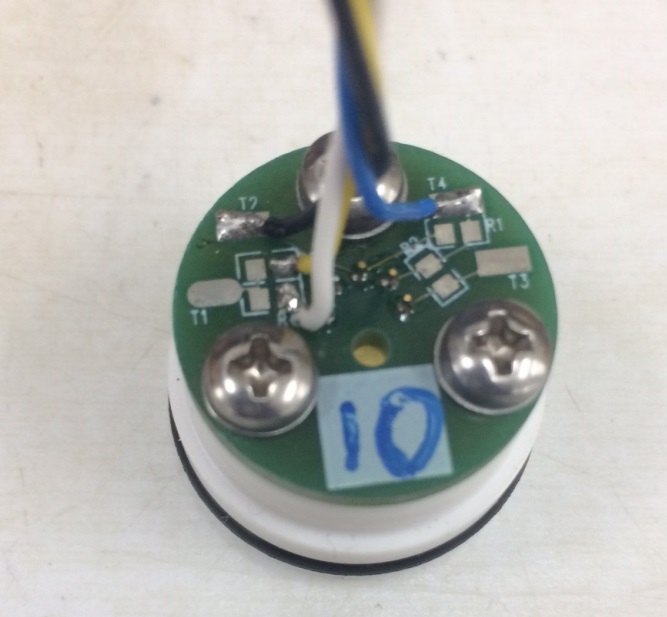
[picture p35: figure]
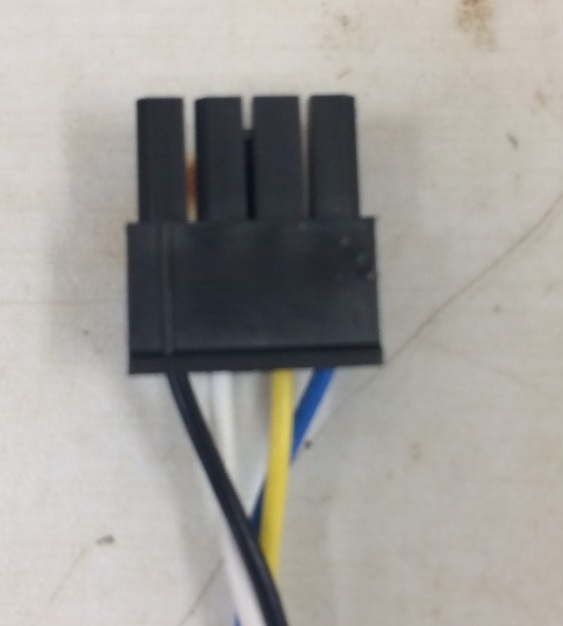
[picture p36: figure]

9. Clean O-ring groove on housing and install O-ring with a small amount of grease.
10. Connect Micro-Fit receptacle to wires after sensor is installed into end cap. The receptacle will not fit through the small hole meant for the sensor wires.

## 1.1. Fluorometer

Fluorometer Label | Description | Wire Color | Wire Color | Pin # on Pop Up Buoy Receptacle
5V | Voltage Supply (5V) | Red | | 1
GND | Ground | Black | | 2
Signal | Analog Signal | Orange | | 3
AGND | Analog Ground | Green | | 4
X10 | x10 Sensitivity | Blue | | 5
X100 | x100 Sensitivity | Yellow | | 6

## 6.5. Camera

## 6.6. Vacuum Port

1. Evenly smear threads of quick-disconnect coupling with ptfe paste.
2. Screw quick-disconnect coupling into end cap. Tighten until threads are fully engaged (hand tight) using 7/16” socket. Do not overtighten, the plastic valve will break easily if ratchetted too quickly or too tight.

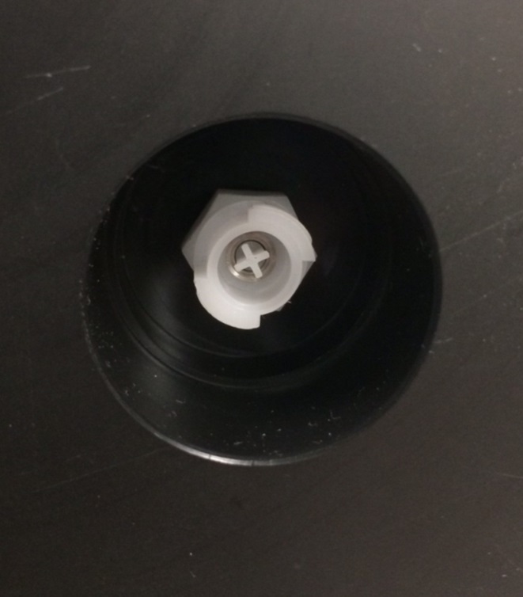
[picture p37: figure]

3. Once programming is complete and unit is ready to be deployed, follow instructions in the User Guide for de-pressurizing the housing and installing the vacuum port cover.

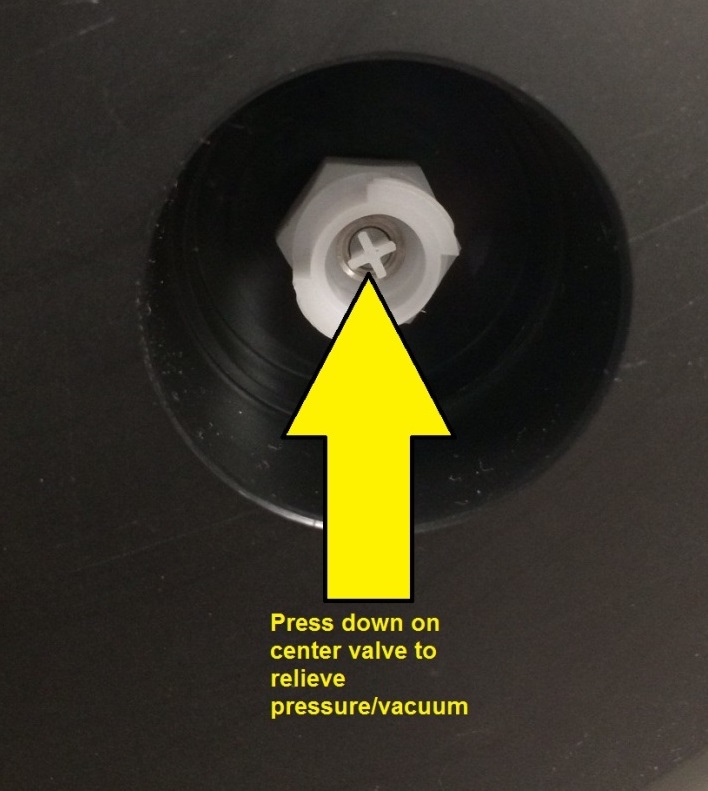
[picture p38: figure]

## 6.7. Printed Circuit Board (PCB)

1. Order PCBs and components (in file Pop-Up 5.3 BOM PCA.xlsx)
2. Assemble PCBs (at Schippers and Crew (http://schippersandcrew.com/))
3. Install coin cell batteries for both RTC and GPS.
4. Install microSD Card
5. Install Arduino MEGA by carefully aligning and pressing down on the headers on the PCB.
6. Test all functionality of all sensors, GPS, and Iridium module. See Section 6.

## 6.8. Electronics Stack, Iridium and GPS Antennae

1. Manufacture and test PCB as described above.
2. Install PCB standoffs and mount to PCB Frame. Do not use plastic standoffs, they will shear off.
3. Insert GPS antenna into rectangular well in bottom of end cap. Place rubber into well so that GPS antenna does not move and rests firmly up against the bottom of the well.
4. Mount PCB frame onto end cap using ¼”x1” hex cap screws, washers, and lock washers.
5. Bundle and zip tie wires from GPS and Iridium antennae so they are clear of O-ring seals and do not get caught when installing and removing the end cap. Also be sure that access to PCB and standoffs is not blocked.

## 6.9. Main Battery Installation

1. Order batteries from A-Pak or other battery retailer.
2. Solder 6-18” of 24-26AWG wire onto the battery leads as needed to ensure there is adequate wire to connect the battery wires to the PCB stack on the end cap after the battery has been installed.
3. Connect Micro-Fit receptacle to battery leads.
4. Order spray-foam insulation from McMaster-Carr. Spray-foam insulation bonds very well to both the trawl float and battery pack. It also becomes very rigid and provides strong support once fully expanded, while adding minimal weight.
5. Set trawl float on a level surface, and brace the float so it does not move while the foam is drying.
6. Set the battery carefully into the bottom of the trawl float, making sure it is as level as possible.
7. Tape the battery wires to the top or outside of the trawl float to prevent the wires from being cemented into the bottom of the float.
8. Please note, the spray-foam can be very messy and has a tendency to keep expanding out of the can, after the trigger has been released. Wear disposable nitrile gloves and be sure that the foam does not drip on O-ring seal surfaces of the trawl float. If any foam does drip, clean it immediately as it will be very difficult to remove without damaging the surface once it has dried.
9. Begin cementing the battery into place with spray foam. The foam will expand to several times its original size and take 30 minutes or more to expand fully. Do not allow the battery to move upwards as the spray foam is expanding. There is not enough reserve space in trawl float and its corners must be contacting the bottom of the trawl float, not resting above it on foam. In order to achieve this, spray the foam in several stages (minimum of 3) and allow the foam to expand and set before spraying more foam. During the first stage of spraying foam, spray a small amount of foam around the 3 bottom corners of the battery pack where it contacts the trawl float and allow the foam to set. This will set the battery pack in place and prevent it from moving during future stages. Once the battery pack is set in place, fill in around the sides and bottom of the battery as best as possible. Lastly, do not allow foam to fill over the top of the center of the battery, such that it will contact the PCB frame and prevent the end cap from seating fully once installed. If possible, spray a small amount of foam around the top corners of the battery to hold it down, but do not reduce the clearance needed for the end cap to seat properly.

## 6.10. Frame

1. Ensure Trawl Float Ear Holes are drilled to 1.00” dia
2. Insert rubber spacers into trawl float ears
3. Connect frame pieces, spacers, and release block
4. Use 5/16” 18-8 Stainless Steel Hardware for connecting all pieces.

## 6.11. Iridium RockBLOCK 9603

The Iridium RockBLOCK 9603 is the satellite communication device for the instrument.

### 6.11.1. Switching RockBLOCK 9603 antenna mode

It's possible to select whether the RockBLOCK 9603 uses the internal patch antenna, or external SMA connector by changing the position of a small RF link cable.The UFL connectors involved are not designed for multiple mating cycles. Repeating this process more than 10 times is likely to cause damage to the UFL connectors and result in poorer RF performance.

1. Remove the 9603 module

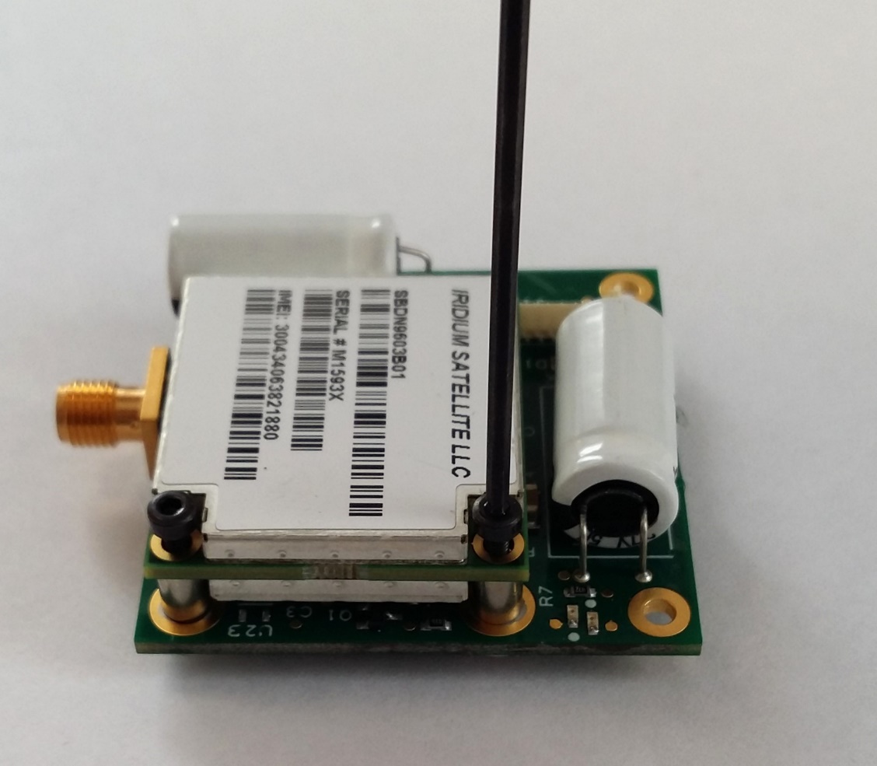
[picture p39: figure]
Remove 9603 Module

Remove 9603 Module

Using a 1.5mm hex driver, remove the two machine screws fixing the 9603 module in place.

Take care!

The 9603 module has a relatively fragile connector. Once the screws are removed, take great care to disengage the connector without twisting or using excessive force.

2. Disconnect the UFL connector from the RockBLOCK PCB

The RF link will be attached to one of two UFL connectors on the RockBLOCK PCB. You need to carefully disconnect this. Do not detach the end of the RF link attached to the 9603 module.

You should use an appropriate UFL removal tool for this task. UFL connectors are not designed for repetitive mating cycles.

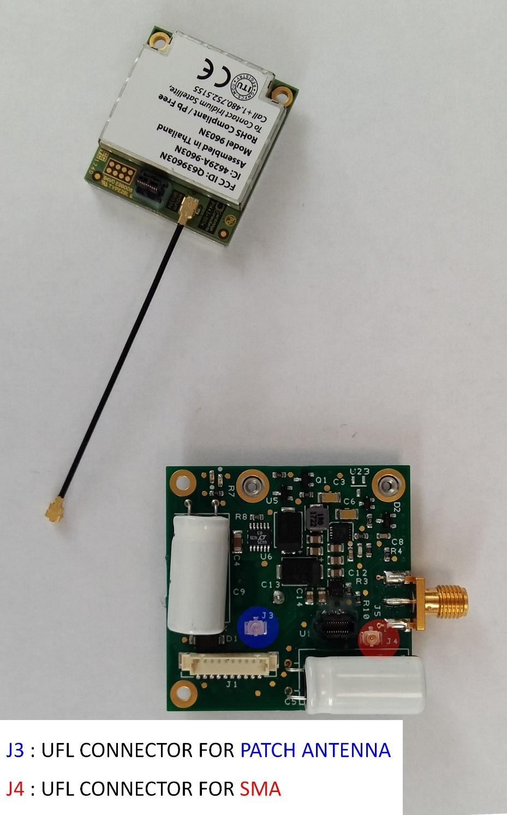
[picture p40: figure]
RockBLOCK PCB Layout

RockBLOCK PCB Layout

Reattach the UFL connector

Select the appropriate UFL connector on the RockBLOCK PCB and reattach the RF link cable. Take care to ensure that the connector mates properly.

Replace the 9603 module

Carefully connect the 9603 module to its header connector. Insert the support pillars. Replace the machine screws.

# 7. Software Development and Programming

## 7.1. Arduino 1.0.6

The Pop-up Buoys were designed and testing using the Arduino 1.8.5 IDE (Integrated Development Environment). The Arduino IDE is a software package that lets users write and upload code directly to the microcontroller on the device. Arduino programs and libraries are mostly written in C or C++. There are some nuances to the devices and libraries, all of which can readily be found online.

Version 1.8.5 should always be used with the Pop-Up buoys unless extensive testing is done to ensure that programs work properly. There are difference in base library packages and the way programs are compiled which may have unpredictable consequences.

## 7.2. Library Changes

The Pop-Up buoys use pre-written libraries for several parts of the software (interfacing with RTC, SD Card, microcontroller pins, etc. This simplifies and accelerates programming a great deal. The downside is that libraries can occasionally have errors or may not be optimized for certain uses in their original form. The following libraries needed to be changed from their original form.

### 7.2.1. Iridium SBD

The updated Iridium SBD library MUST be used for the pop-up buoy to function properly. It is saved as IridiumSBD-1.0-PopUp.

IridiumSBD was a library written by some guy named Mikal Hart to interface Arduino boards with the RockBlock Iridium Module (see web link here (http://arduiniana.org/libraries/iridiumsbd/)). The library vastly simplified integrating the Iridium module with a few exceptions.

1. IridiumSBD should only be used when the RockBlock Serial lines are connected to a hardware serial port on an Arduino. If one attempts to use a software serial port, the Arduino will occasionally miss parsing characters and lock up the program. The Arduino MEGA has 4 hardware serial ports (only one other is used for USB communication), so this does not pose any problems.

2. One user noted about an issue with the doSBDRB() function. Code has been altered in accordance with this suggestion. See below for details:

“I found a bug in doSBDRB() when using a hardware serial port on the Mega 2560. When reading incoming data the for loop is not waiting for data to arrive. I was only getting the first 1 or 2 bytes written to the buffer I passed it. The rest was old data. I made the following changes and it seems to be working:”

This section of the doSBDRB() function in IridiumSBD.CPP now reads as follows. (Changes in bold).

for (int i=0; i= 1000UL * atTimeout)

return ISBD_SENDRECEIVE_TIMEOUT;

}

// if (stream.available())

// {

uint8_t c = stream.read();

if (rxBuffer && prxBufferSize)

if (*prxBufferSize > 0)

{

*rxBuffer++ = c;

(*prxBufferSize)–;

}

else

{

rxOverflow = true;

}

// }

// if (millis() – start >= 1000UL * atTimeout)

// return ISBD_SENDRECEIVE_TIMEOUT;

}

for (int i=0; size > i; ++i)

{

// wait for the data to come in

while (!stream.available())

{

if (cancelled())

return ISBD_CANCELLED;

if (millis() – start >= 1000UL * atTimeout)

return ISBD_SENDRECEIVE_TIMEOUT;

}

uint8_t c = stream.read();

if (rxBuffer && prxBufferSize)

if (*prxBufferSize > 0)

{

*rxBuffer++ = c;

(*prxBufferSize)–;

}

else

{

rxOverflow = true;

}

}

3. Another issue was found with the Pop-Up buoys when receiving messages. Two lines of code were missing at the end of the doSBDRB() function which are needed to process the “OK\r\n” string sent by the iridium module at the end of the iridium response.

After receiving a message, the iridium module will respond with

<<AT+SBDRB[size]____________[checksum]OK\r\n

However, the code only processed up to "…[checksum]". Issuing another command afterwards meant the "OK\r\n" was still in the stream buffer and would not process the next command properly.

This was solved by simply placing a waitForATResponse() after the checksum processes. (No parameters means it only looks for the terminator "OK\r\n").

This section of the doSBDRB() function in IridiumSBD.CPP now reads as follows. (Changes in bold).

uint16_t checksum = 256 * stream.read() + stream.read();

console(F("[csum:"));

console(checksum);

console(F("]"));

// Return actual size of returned buffer

if (prxBufferSize)

*prxBufferSize = (size_t)size;

console("\r\n"); //added this line to skip to next line in terminal

waitForATResponse(); //added this line to process "OK\r\n"

return rxOverflow ? ISBD_RX_OVERFLOW : ISBD_SUCCESS;

### 7.2.2. Software Serial

The updated software Serial library MUST be used for the pop-up buoy to function properly. It is saved as SoftwareSerial-PopUp.

The Pop-Up buoys use the Software Serial library to read and parse NMEA data from the GPS chip. The Software Serial buffer must be increased from 64 to 512 bytes to ensure no data is lost on long NMEA strings. This does use some extra RAM, but the ArduinoMEGA has plenty of reserve memory to accommodate this change. (Can be verified using the MemoryFree library). This is done by simply changing one line in the file SoftwareSerial.h :

#define _SS_MAX_RX_BUFF 512 // RX buffer size //BEFORE WAS 64

# 8. Program Flow

## 8.1. General Program Flow

A. Wake Up
B. Determine mode/phase based on current date/time and programmed cutoff dates/times

0 = Initial programming (before start date)

If mode = 0, display parameters and shut down after user removes USB, don’t take any sample data

1 = Bottom Sample

2 = Wait for Profile

3 = Under Ice

4 = Ice Free

C. Determine next sample time/date and set RTC alarm
D. Collect Sensor Data, Store to SD Card
E. If mode = 1 (Bottom Sample)

Do nothing else, just go to sleep

If mode = 2 (Wait for Profile)

Take initial depth measurement

Continuously take depth readings and compare to initial measurement

Wait for depth to change by m meters

Start profile

Collect profile data at 4 Hz for p seconds

Go to sleep

If mode = 3 (Under Ice)

**This mode is used primarily to preserve battery power if the Pop-Up is expected be under ice for several months after releasing from the bottom. In this mode the unit will only attempt to search for GPS once a day, rather than every hour.**

If hour = 15 (3pm, close to solar noon in most of Alaska)

Search for GPS for g seconds, n times, with delay in between

If GPS lock is found n times

Store GPS location and time on SD Card

Attempt to transmit iridium data

Else

Do nothing else, just go to sleep

If mode =4 (Ice Free)

4. Ice Free

Search for GPS for g seconds, n times, with delay in between

If GPS lock is found n times

Store GPS location and time on SD Card

Attempt to transmit iridium data

Else

Do nothing else, just go to sleep

## 8.2. Iridium Transmission

Once a GPS lock is found, the unit will attempt to transmit messages back via iridium SBD. Data is parsed from the SD Card and transmitted 100 characters at a time. The files are sent back in order of priority (profile data first, followed by under ice data, followed by pre-release bottom data). If the unit sends a message successfully, but then loses Iridium connection before sending all data (which happens often), it will go to sleep, but set the RTC to wake up the unit in 5 minutes, rather than the under ice sample interval. This 5 minute interval is used to get data back more quickly and take advantage of the calm sea state which is likely when the unit first surfaces. After all data is eventually sent, the unit will revert to sending its most recent GPS location and sample data once per day.

Each time the unit transmits a message, it will automatically check for any received messages. Received messages can tell the unit to change file, file position, or the interval of GPS location updates when all data is finished sending. Additionally, every time the unit wakes up and finds a GPS lock, the first message it attempts to send is “Hello!”. This is done in case any files are corrupted, causing the unit to lock up when sending data from the SD Card. In that case, the user may send a message to the unit, skipping to a different file location or file, and hopefully bypassing the corrupt data.

The SD Card will contain 2 files in addition to the data files: filepos.txt and summary.txt. The first unique message the unit attempts to send is summary.txt (simply a list of the files on the card and how long they are, to gauge how successful the unit was and how much data to expect. Filepos.txt is a single line text file used for the unit to remember how far along it is in the transmission process. Its format is “X,NNNNNNNNNNNNN”, where X indicates which file to open and NNNNNNNNNNNNN is the position to start reading the file (simply the number of characters after the start of the file). This is the exact same format for received messages. Values for X are as follows:

‘p’: “prodat.txt”

‘i’: “icedat.txt”

‘b’: “botdat.txt”

‘z’: if the file (or received message) starts with ‘z’, this should mean that the unit has completed sending all data and is now in sleep mode. NNNNNNNNNNNNN will indicate the interval, in seconds, for how long the unit will wait between sending updates on its most recent GPS location and sample data. By default, this is once per day.

## 8.3. Iridium Network - DITCO

In 2015 SBD messages were paid for directly through an account opened with Rock7. In 2017 the SBD payment was transitioned to the PMEL partnership contract with DoD where all Iridium network space was free. In order to take advantage of the DoD Iridium network, all Iridium modems had to be ‘whitelisted’, please refer to section ##

# 9. Programming, Calibrating, and Testing the Units

## 9.1. Program (Sketch) Descriptions

Pop-Up Buoy uses 2 different programs, all described below. The Arduino IDE calls these different programs ‘sketches’.

Setup and Sensor Check (PopUp_5.3_SetupAndSensorCheck.ino)

This program is used during the assembly and testing phases to test that various sensors and utilities on the units are working properly. Once uploaded and the serial monitor is launched, the user is provided a status summary of the unit and a menu to check sensors and utilities one by one. If there are any problems that require changes such as re-connecting a sensor, it is usually necessary to close the serial monitor and re-upload the program. This will allow all sensors to initialize properly.

For details and instructions on using the Setup and Sensor Check Program, see the Pop-Up Buoy User’s Guide.

Deployment (PopUp_Deployment_5.3_Arduino_1.8.5.ino)

This program is used for deployments and calibrations. All deployment parameters (dates, sample intervals, etc.) must be manually entered into the program before uploading.

Once the program is uploaded and the serial monitor is launched, the user will be provided a long dialog confirming deployment parameters and verifying unit status. This dialog should be reviewed carefully for any possible errors.

For details and instructions on configuring units for deployment, see the Pop-Up Buoy User’s Guide.

## 9.2. Uploading Programs (Sketches)

To upload different programs to the Pop-Up Buoy, follow the steps below:

1. Connect all necessary sensors, antennas, coin cell batteries, and micro SD Card to unit electronics.
2. Connect unit to Power Supply (9V Battery or Power Supply with 9V, 1A with power on). Note: Do not use the main battery packs for testing or calibrating as it will deplete power necessary for the final deployment.
3. Connect unit to computer via USB cable
4. Open the Arduino IDE (Integrated Development Environment). Be sure to use version 1.8.5.
5. Open appropriate sketch
6. Select Board
  - Tools → Board → Arduino Mega 2650 or Mega ADK
7. Select COM Port
  - Check Device Manager → Ports to find correct port
  - Tools → Serial Port → COM__
8. Compile Sketch
  - Ctrl + R or Sketch → Verify/Compile
  - Should Read “Done Compiling” when complete
9. Upload Sketch
  - Ctrl + U or File → Upload
  - Should Read “Done Uploading” when complete
10. Launch Serial Monitor
  - Ctrl + Shift + M or Tools → Serial Monitor
  - Note: The baud rate should be set to 115200 (lower right-hand corner after launching Serial Monitor)
  - Note: 9V Power MUST be supplied and turned on before the serial monitor is launched. It is possible to upload sketches without external power, but power must be supplied for sensors to initialize properly when serial monitor is launched.
11. To upload a different sketch, close the serial monitor and begin at Step 5. It is not necessary to disconnect the unit from power or close the Arduino IDE.

## 9.3. Calibrating the Temperature Sensors

The data stored on the SD Card is a voltage reading from one of the unit’s ADC (Analog-to-Digital Converter). The voltage value is fit directly to a Steinhart-Hart curve during the calibration process so that no accuracy is lost by making conversions. Temperature can be calculated using the following equation:

T=1/(A+Blog_10 (x)+C[log_10 (x)]^3) - 273.15

Where:

T = Temperature in °C

x = ADC reading

A,B, and C = Steinhart-Hart Coefficients

The simplest way to program the unit to calibrate the temperature sensors is to use the deployment program and just have the unit take samples as if it were on the bottom waiting for release. Calibrations should always be done using a sample interval of 30 seconds – shorter sample intervals may cause small errors due to self-heating in the thermistor.

1. Follow procedures in section 6.1 to upload the sketch named PopUp_5.3_SetupAndSensorCheck.ino.
2. Set the RTC (Enter ‘2’ to set RTC time/date.) Ensure the RTC is synchronized with the clock on the temperature bath.
3. Check that RTC is keeping time (Enter ‘1’ – display Status)
4. Check that SD Card is connected and communicating properly (Enter ‘1’ – display Status)
5. Test the Thermistor probes to ensure it is connected and responding to temperature changes. A response should be visible just by holding the probe between 2 fingers.
6. Verify that the Temperature Reference is reading appropriate values. (Should be approximately 50 kOhms)
7. Close the Serial Monitor
8. Follow procedures in section 6.1 to upload the sketch named PopUp_Deployment_5.3_Arduino_1.8.5.ino
9. Set the value for BOTTOM_SAMPLE_INTERVAL to 30 seconds (within #define statements, line 42)
10. Set unitStart to an appropriate time in the near future
11. Set releaseTime to a time long after the calibration will be over. There is no risk of running out of storage space on the SD Card.
12. Compile the sketch (Ctrl + R or Sketch → Verify/Compile)
13. Upload the sketch (Ctrl + U or File → Upload)
14. Launch the Serial Monitor (Ctrl + Shift + M or Tools → Serial Monitor)
15. Carefully read the deployment dialog and verify all settings
16. Disconnect the unit from USB cable
17. Connect to 9V power (battery or power supply) before the unitStart time/date
  a. The unit can be temporarily disconnected from power as long as it is reconnected before the unitStart time/date. This way, multiple units can be connected and run off a single power supply for the calibration if desired.
18. Immerse temperature probes in temperature bath and start temperature bath program
19. Once temperature bath program has completed, download data from SD Card and process data
  a. Open a previous calibration file to see instructions and examples of how to process calibration data. Always use Paste Values.
    i. Download .CAL file from temperature bath computer
    ii. Follow numbered instructions on sheet TBxxxxx to process .CAL file
    iii. Format data from individual Pop-Up units and input into PopUpTempCal_xxx sheets. Follow numbered instructions and add new sheets if needed
    iv. Paste data into TempCalSummary Sheet and run genssh Macro for each unit
20. Record calibration coefficients. Store data and coefficients from temperature calibration for records and post processing data. (Data transmitted by the Pop-Up buoys is uncalibrated.)

## 9.4. Calibrating the PAR Sensor

The data stored on the SD Card is a voltage reading from one of the unit’s ADC (Analog-to-Digital Converter). The PAR Sensor is a photodiode which outputs a small current which is proportional to the amount of light hitting the sensor. The sensors are calibrated by the manufacturer and provide a known current output vs. incoming PAR.

PAR can be calculated using the following equation:

PAR=(y-y_0 )*0.000668268/m*1/0.73

Where:

PAR = photosynthetically active radiation (in molm⁻²s⁻¹)

y = ADC reading

y0 = ADC reading at 0 molm⁻²s⁻¹

m = calibration from manufacturer (uA/molm⁻²s⁻¹)

0.000668268 is a fixed conversion factor for the circuit which converts voltage to current. Details on this can be found in the document PAR circuit calculations - Rev 5.3.xlsx.

0.73 is a scaling factor to account for the amount of light that is absorbed/reflected by the acrylic housing. This was found experimentally by comparing a calibrated Satlantic PAR sensor to several Pop-Up buoy PARs mounted together and exposed to identical light conditions.

The only factor that must be calibrated is y0. This is found by exposing the sensor to zero light and measuring the response. This is most easily done by using the SetupandSensorCheck sketch and recording the response from the PAR sensor with the end cap placed upside down on a black surface (no incoming light).

## 9.5. Calibrating the Fluorometer

See EcoFOCI_PopUp\Engineering\Sensors\Turner Cyclops Fluorometer

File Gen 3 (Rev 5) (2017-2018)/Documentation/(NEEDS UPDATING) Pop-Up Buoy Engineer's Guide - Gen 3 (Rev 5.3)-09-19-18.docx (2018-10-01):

# Pop-Up Buoy Engineer’s Guide

# (Gen 3/Rev 5.3)

Table of Contents

# 1. Background

The Pop-Up Buoy was developed as a unique product designed to take measurements while sitting under sea ice in the Arctic - to fill the gap in available technology between year-round deeper moorings and surface-based sampling in the summers. Measuring just under sea ice is of particular interest because the conditions there play a critical role in shaping one of the world’s most highly productive eco-systems. However, because of the harsh and unpredictable environment of shifting and breaking ice, actually acquiring measurements close to the ice during the Winter and Spring without losing instruments has been notoriously difficult. Because of the unique conditions, it needed to be robust, inexpensive, and expendable, but sophisticated enough to acquire oceanographic-quality data.

Cost was by far the driving factor in most of the design decisions and led to some atypical outcomes, such as the independent burn wire release and stripped down sensors. Since the floats only provide 1 profile of the water column, it was desirable to keep the cost around $3,000 per float. From a program-level perspective, the extremely low cost (compared to other instruments) is what makes the instrument a viable option for collecting data.

The instruments are designed to be deployed from a research vessel during the ice-free season, where they remain anchored on the bottom for many months until the surface is completely covered in sea ice. At a designated time for each device, a timed release is triggered which allows the buoys to float upward in the water column, collecting a vertical profile of the water column, until they reach the ice. The buoys remain under the ice until they are forced out by break-up and melting, transmitting their data to shore via satellite when they do arrive at the surface.

This third generation of instruments measures temperature, Sea Surface Temperature (when drifting at surface), PAR, Depth, and fluorescence (optional). It also has GPS and Iridium modules for location and transmission.

# 2. Design Decisions

## 2.1. Burn-Wire Release

## 2.2. Sensors

### 2.2.1. Temperature Sensor

### 2.2.2. PAR Sensor

The PAR sensor used on the Pop-Up buoys is a TAG-PARQ by Skye Instruments. This is the same sensor as used on the initial prototype of the Pop-Up Buoys and integrated into the satellite tag provided by the University of St. Andrews. It was shown to have excellent response, even in very low light conditions.

The TAG-PARQ sensor costs only $340 whereas the least expensive alternative (a LICOR PAR sensor) is around $800.

One tradeoff for this sensor is that the TAG-PARQ is a simple photodiode with an analog output in µAs. An amplifier circuit is built into the main electronics to properly amplify and convert the signal.

A second tradeoff for the TAG-PARQ sensor is that it is not waterproof and must be installed in a separate housing. Ideally, this should be a perfect cosine diffuser so the angle of incident light does not affect the signal. The acrylic housing used in the Pop-Up buoys is not a perfect cosine diffuser, but works well within the 3% margin of error the sensors are calibrated for. Testing showed the acrylic absorption by acrylic can be easily corrected for with a calibration factor, multiplying the measured signal by 1.15.

The graphs below show an example of how the PAR sensors perform compared to a commercial instrument in low light conditions and in response to changing the incident angle of light.


### 2.2.3. Pressure Sensor

The Pop-Up Buoys have a Keller PA-4LD OEM Pressure Transmitter (http://www.keller-druck.com/picts/pdf/engl/4ld_9ld_e.pdf) with embedded signal conditioning that measures pressure. It output digital data using I²C communication and does not require any calibration. It is very accurate sensors (0.7% FS) for a cost of only ~$120 each. These are the same sensors used on PMEL’s Prawler, so both the housing and small attachment PCB were taken directly from Prawler designs.

### 2.2.4. GPS

The GPS Chosen for the Pop-Up buoys is a low power, low cost GPS Module. It is the same module used on Adafruit’s Ultimate GPS Breakout (https://learn.adafruit.com/adafruit-ultimate-gps/overview). This made it an easy choice for prototyping and rapid development, but the module also has excellent sensitivity, time-to-fix, and power requirements – all at low cost. The modules can be purchased from 3rd party sellers such as Adafruit, but are less expensive if purchased directly from the manufacturer.

### 2.2.5. Iridium Module

The Iridium Module used in the Pop-Up buoys is a RockBLOCK 9603 (https://www.rock7mobile.com/products-rockblock.php). This device is a very low cost SBD (Short Burst Data) Iridium module. Once again, cost was the main driver for choosing this module as they cost only approximately $250 each. Additionally, the modules were made to interface quickly and easily with controllers such as the Arduino boards and can be powered with only 5V DC. Avery thorough IridiumSBD library (http://arduiniana.org/libraries/iridiumsbd/) was also developed specifically for using the RockBLOCK with an Arduino board, which also facilitated prototyping. Note: Some minor, but critical modifications were made to the IridiumSBD library for the Pop-Up buoys – refer to section 4.2.1 for more details.

The RockBLOCK 9603 allows for 2-way communication with the Pop-Up Buoys. Once the buoys surface, users are able to send commands to re-send any data that is lost or to adjust the interval of position updates once all data has finished sending.

## 2.3. Mechanical Design

### 2.3.1. Trawl Float

12” Trawl floats are used for the Pop-Up Buoy’s main housing because they are very inexpensive, machine well, and the shape is ideal for under the ice. The round and robust housing should is designed to ‘ride’ under the ice, where traditional instruments are easily destroyed. The trawl floats cost only around $35 and are nominally rated for a depth of 600 fathoms (1097meters).

### 2.3.2. End Cap

The end cap design is used to consolidate all electronics and sensors into a single package and protect the instrument’s sensors and antennas. Once the electronics package and sensors are assembled together in the end cap, it can be easily assembled or removed as needed for testing and deployment.

All sensors are either flush with the upper surface of the end cap or slightly below to protect them from damage under the ice. This is critical for this instrument. Additionally, the GPS and Iridium antennas are actually mounted under the end cap, further protecting them. These antennas on other instruments are typically very vulnerable to damage or icing, leading to instrument failure. The interference from the end cap does attenuate and distort the communication slightly, but the cap is thin enough that both GPS and Iridium work effectively.

The End Cap has 2 o-ring seals for extra security: One face seal and one piston seal. The trawl floats are too thin to place two piston seals on the cap. The end cap is a half-dovetail groove because the o-ring is in between sizes and the dovetail is needed to hold the o-ring in place while assembling.

A vacuum port is placed in the end cap which is used to pump air out of the float once sealed. This creates a vacuum inside the float and holds the end cap on firmly. A vacuum of ~10psi provides ~300 lbs of force holding the cap down. There is a pressure relief valve on the center of the valve which should be used to relieve pressure when disassembling the float.

### 2.3.3. Frame

## 2.4. Electronics

### 2.4.1. Arduino MEGA

The Arduino MEGA was used in the design of this instrument primarily to simplify the design process (that and the principal engineer was not formally trained in electronics, thus had to make some accessions). The Arduino platform is an open-source development platform, which combines a micro-processor, some fundamental software libraries, and a programming environment to make it very easy for newcomers to develop electronics equipment. Since the Arduino is open-source, there are volumes of information online about the specifics which will not be discussed here. The Arduino MEGA is one of many Arduino boards and was chosen because a) it has more input/output pins necessary to control the various signals for this instrument and b) it has extra hardware Serial ports, which are required for the Iridium module.

One main drawback of using the Arduino platform is power consumption. When the Pop-Up Buoy is just sampling sensors, it draws ~80mA. Other simple oceanographic instruments often draw less than 10 mA. This is still tolerable, because the instrument only needs to be on for a short time before going back to sleep. Also, the amount of power required to search for GPS and power the Iridium module while sending messages accounts for the majority of the required power budget and would be necessary regardless of what micro-controller were used.

One other major consideration must be made because the Arduino MEGA also does not have a ‘low-power’ mode. In order to overcome this problem, the Arduino is completely shut down when not sampling. As the Arduino cannot ‘wake itself up’, a RTC with a built in alarm is used to send a signal to a power converter and wake the unit. This is not a traditional or even optimal design, but it does work for the application, keeps cost down, and has proven a reliable method in several other projects (MTR-Duino and TAPS Controller).

In the future, it may be desirable to switch the design to a standard processor used for oceanographic instruments. This would have a few main advantages – a) lower power consumption when sampling, b) smoother communication with terminal programs (Arduinos can be a bit finicky), and c) a more standardized instrument which doesn’t require unique software or equipment. PMEL’s EDD should be consulted or included if choosing to this approach in order to optimize and standardize the equipment as best as possible.

### 2.4.2. RTC

The Pop-Up Buoy uses a DS3234 RTC with an internal alarm to ‘wake up’ the unit from sleep at prescribed sample intervals. This is done because the Arduino does not have an on-board clock to do so and must be shut down to conserve power. The alarm is set within the program using the appropriate registers according to the DS3234 datasheet. The Shutdown pin on the LT1129 allows the Arduino MEGA to be completely shut off and then woken with a signal from the RTC.

### 2.4.3. Batteries

Standard D-Cell Alkaline Batteries are used for the Pop-Up Buoy, primarily to reduce cost. The additional weight of the alkaline batteries at the bottom of the trawl float is advantageous as it helps to keep the unit upright. The primary voltage regulator requires a minimum 5.5V input, so a 9V pack is used to allow for both de-rating for temperature effects and voltage drop as the battery is drained.

The majority of power is consumed when the unit is on the surface, searching for GPS and sending Iridium messages. See power budget spreadsheet for calculations and programming description for more on power-saving measures.

Battery packs can be obtained from A-Pak batteries (425-820-2272). The first packs cost only ~$100 each.

### 2.4.4. Temperature Circuit

The temperature circuit used in this design was adapted from the original MTR (Miniature Temperature Recorder) designed by PMEL. The original MTR used a circuit with a shunt regulator and operational amplifier connected to the thermistor, which produced a voltage sent to a voltage-to-frequency converter, which was finally counted by the micro-processor. In the years since the original design, electronics have seen some marked advances in many areas – one of them being with Analog to Digital Converters. The ADS1100 ADC used in the Pop-Up Buoy is a self-calibrating ADC capable with 0.02% accuracy. This is just slightly less than the 0.01% accuracy needed to achieve the 0.01°C design requirement, so a 0.01%, 0.2ppm reference resistor is used not only to track any drift in the sensor, but also to correct for any inaccuracy in the ADC.

# 3. Circuit Description

## 3.1. Arduino Mega

The heart of the Pop-Up Buoy Controller is an Arduino MEGA 2650 (https://www.arduino.cc/en/Main/arduinoBoardMega2560) which controls read and write functions to various ICs, collects and stores sensor data, and communicates with the GPS and Iridium Modules. It uses I²C and SPI communications as well as digital signals for ICs and sensors, and two hardware serial lines for GPS and Iridium communications.

## 3.2. Power Regulation

Power is regulated and switched on and off with an LT1129 Micro-power Low Dropout Regulator with Shutdown (http://cds.linear.com/docs/en/datasheet/112935ff.pdf) (U21). The LT1129 provides 5V power to the board and only consumes 16µA in shutdown mode (when unit is sleeping between samples).

Both the RTC and Arduino MEGA are connected to the Enable pin on the LT1129. When waking up, the RTC alarm pulls the Shutdown signal high, turning on power to the unit. The Arduino Micro then sends a high signal via the ‘Shutdown’ Pin which keeps the unit running while the alarm is reset and sampling is completed. Eventually, the Arduino Micro sends a low voltage signal via the ‘Shutdown’ pin, forcing the Enable signal low and shutting off power to the unit. R26 is a pull down resistor to ensure the Enable signal is normally low.

3.3V power is needed for the RTC, microSD Card, Accelerometer, and I²C communication with the ADCs and is provided by U18, an LP5907 Ultra-Low Quiescent Current LDO (http://www.ti.com/lit/ds/symlink/lp5907.pdf). The Arduino MEGA does contain an onboard 3.3V regulator, but is bypassed to prevent drawing too much current through the Arduino and destroying the board.

Several AO3407A P-Channel MOSFET Transistors (http://www.aosmd.com/pdfs/datasheet/AO3407A.pdf) are used to toggle power to the 5V sensors (Q5), 3.3V Sensors (Q4), GPS (Q6), and Iridium module (Q3), in order to minimize power consumption. Pullup resistors (R19, R20, R22, and R24) ensure the input signal is normally high (power off) and a low voltage signal from the Arduino MEGA turns power on to each when needed. Current limiting resistors R17, R18, R21, and R23 are used for the digital signals to reduce current consumption flowing from the Arduino MEGA and avoid exceeding its maximum.

## 3.3. MicroSD Card, Accelerometer, and RTC

The microSD Card, Accelerometer, and RTC require SPI communications at 3.3V and the Arduino MEGA operates at 5V. U15, a MC74VHC1GT125 Non-Inverting Hex Buffer (http://www.ti.com/lit/ds/symlink/cd74hc4049.pdf) which accepts over voltage inputs, is used to lower voltages coming from the Arduino (SCK, MOSI, CS) and U14, a NC7S14 Single Non-Inverting CMOS Logic Level Shifter (http://www.onsemi.com/pub_link/Collateral/MC74VHC1GT125-D.PDF), is used to raise the MISO signal going to the Arduino MEGA.

U15 is a standard microSD Card Push-Push Socket (http://www.molex.com/pdm_docs/sd/473340001_sd.pdf) to allow the user to remove the card and download data quickly for testing and calibration, or if a unit is ever recovered.

U17 is an ADXL345 3-Axis Digital Accelerometer (http://www.analog.com/media/en/technical-documentation/data-sheets/ADXL345.pdf). Its high resolution enables measurement of inclination changes less than 1.0° and is used to measure the angle of the Pop-Up Buoy from vertical. U10, a SN74LVC1G32 Single 2-Input Positive OR Gate (http://www.ti.com/lit/ds/symlink/sn74lvc1g32.pdf), is recommended for the ADXL345 to prevent bus traffic from accidentally appearing as an I²C start command.

U20 is a DS3234 Extremely Accurate Temperature Compensated RTC (http://datasheets.maximintegrated.com/en/ds/DS3234.pdf) which provides both timekeeping function and an alarm to wake the unit up and collect samples at the proper time. B2, a 12mm lithium coin cell battery, powers the RTC when the unit’s primary power is off. U19, an NC7S14 High Speed Inverter with Schmitt Trigger Input (https://www.fairchildsemi.com/datasheets/NC/NC7S14.pdf), is used to invert the signal coming from the RTC alarm to be the proper voltage for the Shutdown input of the primary voltage regulator, U21.

When the alarm function on the RTC is not active, the INT/SQW pin is held at high impedance. This keeps the input signal to U19 at high voltage, and the output to the Enable pin low (power off). R28 is a pullup resistor to ensure the input signal to U3 is normally high. R29 is a voltage dividing resistor to keep the high side of R28 at an acceptable level for U19. When the alarm function is triggered, the INT/SQW pin on the RTC drops to low impedance, allowing current to flow and driving the input of U3 to low voltage. This causes the output of U19 to be high voltage and the high signal sent to the Shutdown pin turns power to the unit on. U19 and R28/R29 are tied to the primary battery, rather than to the coin cell, to prevent the coin cell battery from draining if the alarm is triggered, but the primary battery is dead or not connected. After all, the alarm function is only needed if the primary battery is available.

D2 and D3 are Schottky Diodes that ensure the shutdown signal coming from the Arduino and shutdown signal coming from U19 do not cause a short. The low forward voltage of the Schottky (450 mV) keeps the voltage at the Shutdown pin at the highest possible voltage to ensure the primary voltage regulator trips on.

## 3.4. Temperature Measurement

The voltage measurement for temperature is done by U6, an ADS1100 Self-Calibrating 16-Bit ADC (http://www.ti.com/lit/ds/symlink/ads1100.pdf), which achieves approximately 0.02% absolute accuracy using the settings in this instrument. The ADC requires a highly accurate power source, provided by U4, a MAX6126 Ultra-High-Precision Voltage Reference (http://datasheets.maximintegrated.com/en/ds/MAX6126.pdf).

The ADC requires I²C communications at ~3V and the Arduino Micro operates at 5V. Q1, Q2, and R5, R7, R9, and R11 are used provide bi-directional I²C communications at the proper voltages. The I²C communications are tied to 3.3V rather than 3V to keep the ADC on an isolated circuit and because the ADC/communication protocol can tolerate the small difference in voltage.

The analog portion of the circuit was adapted from the original MTRs (Miniature Temperature Recorders) designed at PMEL. It provides an almost perfectly linear voltage output between 0.05V and 1.05V when the thermistor is between -5°C (~42kΩ) and +60°C (~2kΩ). The non-linear portion is only at higher temperatures where higher accuracy is not normally needed in oceanographic applications. (See the LTSpice model for more specific info). After the voltage signal is output by an LT1013 Precision Operational Amplifier (http://www.ti.com/lit/ds/symlink/lt1013.pdf), a gain of 2 is applied internally by the ADC before sending the digital signal to the Arduino Micro. During calibration, the voltage measurement is directly fit to a Steinhart-hart equation, so conversion to resistance or any other values is not needed.

A 0.1°C interchangeable NTC thermistor is used, which can provide 0.1°C accuracy by using calibration coefficients from a different unit. This is advantageous if calibration is not possible for some reason, or calibration info is lost or corrupted. On the Printed Circuit Board, the analog circuit elements are on a separate isolated ground plane, linked to the main ground plane only by one small trace. This is done to reduce any potential ground noise from digital signals in the rest of the circuit.

Since 0.01°C accuracy was needed for this application, but the ADC and voltage reference can only provide ~0.02°C accuracy (~0.02%), R12, an ultra-high precision reference resistor with 0.01% tolerance and ±0.2ppm temperature coefficient, is used to correct for any inaccuracy. U7, an ADG836 Dual SPDT Switch (http://www.analog.com/media/en/technical-documentation/data-sheets/ADG836L.pdf), is used to swap out the thermistor and reference resistor in order to take the alternate measurement. Low on-state resistance and tight channel-to-channel matching make this switch optimal for providing consistent measurements. The resistors are swapped out by a single digital signal sent from the Arduino Micro which is translated to 3.3V by U5, a NL17SZ07 Single Non-Inverting Buffer with Open Drain Output (http://www.onsemi.com/pub_link/Collateral/NL17SZ07-D.PDF). R10 is a pullup resistor to make sure the output voltage is normally high and does not float.

## 3.5. PAR Measurement

The voltage measurement for the PAR sensor is done by U2, another ADS1100 Self-Calibrating 16-Bit ADC (http://www.ti.com/lit/ds/symlink/ads1100.pdf). This ADC is on an isolated, highly accurate power source – U1, also a MAX6126 Ultra-High-Precision Voltage Reference (http://datasheets.maximintegrated.com/en/ds/MAX6126.pdf). Both ADS1100 ADCs are tied to the same I²C bus and are identified by unique addresses (determined by unique part numbers when purchasing).

The analog portion of the PAR circuit is a trans-impedance amplifier, designed following the example in TI Designs TIDU535 Verified Design (http://www.ti.com/lit/ug/tidu535/tidu535.pdf)

The TAG-PARQ sensor is a simple photodiode, which outputs a small but precise current when light at the proper frequency strikes the face of the sensor. R2 and R3 form a voltage divider, biasing the non-inverting input of the op amp at 0.5V. The op amp, U3, is an ISL 28134 Ultra Low Noise, Zero Drift Rail-to Rail Precision Op Amp (http://www.intersil.com/content/dam/Intersil/documents/isl2/isl28134.pdf) – the 15nV°/C offset drift for this sensor is critical in order to not affect the small signal that is output by the TAG-PARQ sensor. Biasing the non-inverting input at 0.5V is also important to account for the maximum initial offset voltage of the op amp. R1 sets the gain of the circuit at 137,000 – providing a nominal 0.5V to 2.5V signal at the input of the ADC for PAR values of 0 to 1000 µmolm⁻²s⁻¹.

See the ‘PAR Circuit Calculations’ spreadsheet and the LT Spice model for more specific information.

## 3.6. Pressure Measurement

The Pop-Up Buoys have two Keller PA-4LD OEM Pressure Transmitters (http://www.keller-druck.com/picts/pdf/engl/4ld_9ld_e.pdf) with embedded signal conditioning that measure pressure. The pressure sensors are connected to the same I²C bus as the ADCs and simply provide a digital value for pressure to the Arduino MEGA.

When obtained from the manufacturer, these pressure transmitters have identical I²C addresses and one must be altered to avoid communication problems. Information on how this is done is contained in the Communication Protocol document (http://www.keller-druck2.ch/swupdate/InstallerD-LineAddressManager/manual/Communication_Protocol_4LD-9LD_en.pdf) and explained in Section 6.1.

## 3.7. GPS

GPS acquisition is done by U9, a GlobalTop Technology FGPMMOPA6H Standalone GPS Module (https://cdn-shop.adafruit.com/datasheets/GlobalTop-FGPMMOPA6H-Datasheet-V0A.pdf). As soon as power to the module is switched on, it begins searching for a GPS signal and outputs serial data as NMEA output sentences, which is parsed and processed by the Arduino MEGA. Since the GPS module operates at 3.3V and the Arduino MEGA operates at 5V, U8, a NC7S14 Single Non-Inverting CMOS Logic Level Shifter (http://www.onsemi.com/pub_link/Collateral/MC74VHC1GT125-D.PDF), and U11, a TX and RX 3.3V to 5V – U8 and U11, a NL17SZ07 Single Non-Inverting Buffer with Open Drain Output (http://www.onsemi.com/pub_link/Collateral/NL17SZ07-D.PDF) are used to translate the serial data to the appropriate voltages.

B1, a 12mm lithium coin cell battery provides backup power to the GPS, which allows the unit to retain memory of previous satellite information and acquire a position lock more quickly.

The GPS unit also uses a 28dB Active External Antenna (https://www.adafruit.com/products/960) which is embedded in the end cap and connected to the SMA connector, J5.

## 3.8. Iridium Module (RockBLOCK Mk2)

Iridium communications are completed by an external RockBLOCK Mk2 (https://www.rock7mobile.com/products-rockblock.php) module which is mounted to the main board. The iridium module communicates with the Arduino MEGA using one of the MEGA’s hardware serial ports. Apart from power and serial communications, the only other connection needed for the RockBLOCK is a digital signal to the unit’s On/Off pin which is used to toggle whether it is awake or asleep. A current limiting resistor, R25, is used for the signal to reduce current consumption flowing from the Arduino MEGA and avoid exceeding its maximum.

# 4. Construction and Assembly

## 4.1. Temperature Sensor

1. Connect Micro-Fit receptacle to wires

## 4.2. PAR Sensor

1. Machine acrylic housing per specifications.
2. Solder 6-8” of 24-26AWG wire onto the two sensor leads. Be careful to observe polarity and connect the cathode (-) of the PAR sensor to the black wire.
3. Set PAR sensor into housing on a flat working surface with leads facing upwards.
4. Glue PAR Sensor into place using 2 part quick set epoxy. Use a very small amount of epoxy at first to glue the bottom corner between the PAR sensor and housing first. This will ensure the small gap between the sensor and housing is sealed and that no epoxy will leak down onto the white photo-sensitive portion of the sensor.

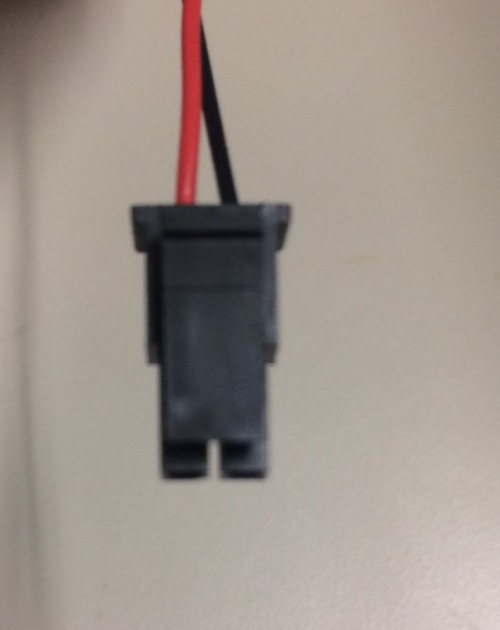
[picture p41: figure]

5. After epoxy has fully set, connect Micro-Fit receptacle to wires. The hole drilled for the PAR sensor wires is large enough for the receptacle to fit through.
6. Clean O-ring grooves and install O-rings with a small amount of grease.
7. When uninstalling PAR sensor, use an awl or similar tool to push the edge of the acrylic housing out of the end cap from the bottom.

## 4.3. Pressure Sensors

1. Machine pressure housing per specifications.
2. Order small pressure sensor PCBs, or get spare PCBs from Prawler parts. The pressure sensor and housing is the exact same as used on the Prawler. (Keller 4-LD)
3. Mount pressure sensor into housing using a small amount of grease on the O-ring.
4. Mount pressure sensor PCB onto back of housing using screws.
5. Solder leads from pressure sensor onto PCB.
6. Solder 6-8” 24-26 AWG wires to PCB. The sensor uses a simple 4 wire connection to the main Pop-Up board, with no resistors or other components needed. The 4 wires and pin-outs are shown below. This information is also shown on the pressure sensor data sheet. Wire colors have been preserved to avoid any confusion.


7. Clean O-ring groove on housing and install O-ring with a small amount of grease.
8. Connect Micro-Fit receptacle to wires after sensor is installed into end cap. The receptacle will not fit through the small hole meant for the sensor wires.

## 4.4. Vacuum Port

1. Wrap threads of quick-disconnect coupling with Teflon tape.
2. Screw quick-disconnect coupling into end cap. Tighten until threads are fully engaged (hand tight) using 7/16” socket.


3. Once programming is complete and unit is ready to be deployed, follow instructions in the User Guide for de-pressurizing the housing and installing the vacuum port cover.


## 4.5. PCB

1. Order PCBs and components (in file Pop-Up 5.3 BOM PCA.xlsx)
2. Assemble PCBs (at Schippers and Crew (http://schippersandcrew.com/))
3. Install coin cell batteries for both RTC and GPS.
4. Install microSD Card
5. Install Arduino MEGA by carefully aligning and pressing down on the headers on the PCB.
6. Test all functionality of all sensors, GPS, and Iridium module. See Section 6.

## 4.6. Electronics Stack, Iridium and GPS Antennae

1. Manufacture and test PCB as described above.
2. Install PCB standoffs and mount to PCB Frame. Do not use plastic standoffs, they will shear off.
3. Insert GPS antenna into rectangular well in bottom of end cap. Place foam into well so that GPS antenna does not move and rests firmly up against the bottom of the well.
4. Mount PCB frame onto end cap using ¼”x1” hex cap screws, washers, and lock washers.
5. Bundle and zip tie wires from GPS and Iridium antennae so they are clear of O-ring seals and do not get caught when installing and removing the end cap. Also be sure that access to PCB and standoffs is not blocked.

## 4.7. Main Battery Installation

1. Order batteries from A-Pak or other battery retailer.
2. Solder 6-18” of 24-26AWG wire onto the battery leads as needed to ensure there is adequate wire to connect the battery wires to the PCB stack on the end cap after the battery has been installed.
3. Connect Micro-Fit receptacle to battery leads.
4. Order spray-foam insulation from McMaster-Carr. Spray-foam insulation bonds very well to both the trawl float and battery pack. It also becomes very rigid and provides strong support once fully expanded, while adding minimal weight.
5. Set trawl float on a level surface, and brace the float so it does not move while the foam is drying.
6. Set the battery carefully into the bottom of the trawl float, making sure it is as level as possible.
7. Tape the battery wires to the top or outside of the trawl float to prevent the wires from being cemented into the bottom of the float.
8. Please note, the spray-foam can be very messy and has a tendency to keep expanding out of the can, after the trigger has been released. Wear disposable nitrile gloves and be sure that the foam does not drip on O-ring seal surfaces of the trawl float. If any foam does drip, clean it immediately as it will be very difficult to remove without damaging the surface once it has dried.

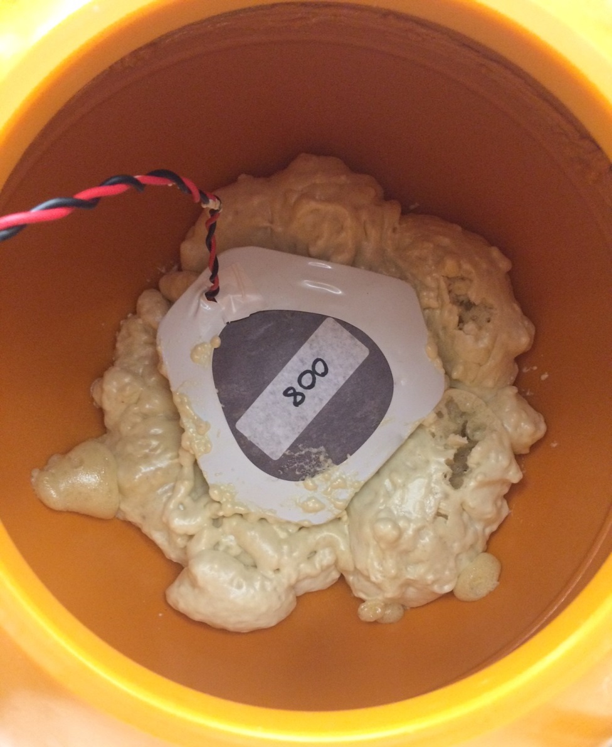
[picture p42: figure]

9. Begin cementing the battery into place with spray foam. The foam will expand to several times its original size and take 30 minutes or more to expand fully. Do not allow the battery to move upwards as the spray foam is expanding. There is not enough reserve space in trawl float and its corners must be contacting the bottom of the trawl float, not resting above it on foam. In order to achieve this, spray the foam in several stages (minimum of 3) and allow the foam to expand and set before spraying more foam. During the first stage of spraying foam, spray a small amount of foam around the 3 bottom corners of the battery pack where it contacts the trawl float and allow the foam to set. This will set the battery pack in place and prevent it from moving during future stages. Once the battery pack is set in place, fill in around the sides and bottom of the battery as best as possible. Lastly, do not allow foam to fill over the top of the center of the battery, such that it will contact the PCB frame and prevent the end cap from seating fully once installed. If possible, spray a small amount of foam around the top corners of the battery to hold it down, but do not reduce the clearance needed for the end cap to seat properly.

## 4.8. Frame

1. Ensure Trawl Float Ear Holes are drilled to 1.00” dia
2. Insert rubber spacers into trawl float ears
3. Connect frame pieces, spacers, and anodes as shown in exploded view shown below
4. Use 5/16” 18-8 Stainless Steel Hardware for connecting all pieces.

# 5. Software Development and Programming

## 5.1. Arduino 1.0.6

The Pop-up Buoys were designed and testing using the Arduino 1.8.5 IDE (Integrated Development Environment). The Arduino IDE is a software package that lets users write and upload code directly to the microcontroller on the device. Arduino programs and libraries are mostly written in C or C++. There are some nuances to the devices and libraries, all of which can readily be found online.

Version 1.8.5 should always be used with the Pop-Up buoys unless extensive testing is done to ensure that programs work properly. There are difference in base library packages and the way programs are compiled which may have unpredictable consequences.

## 5.2. Library Changes

The Pop-Up buoys use pre-written libraries for several parts of the software (interfacing with RTC, SD Card, microcontroller pins, etc. This simplifies and accelerates programming a great deal. The downside is that libraries can occasionally have errors or may not be optimized for certain uses in their original form. The following libraries needed to be changed from their original form.

### 5.2.1. Iridium SBD

The updated Iridium SBD library MUST be used for the pop-up buoy to function properly. It is saved as IridiumSBD-1.0-PopUp.

IridiumSBD was a library written by some guy named Mikal Hart to interface Arduino boards with the RockBlock Iridium Module (see web link here (http://arduiniana.org/libraries/iridiumsbd/)). The library vastly simplified integrating the Iridium module with a few exceptions.

1. IridiumSBD should only be used when the RockBlock Serial lines are connected to a hardware serial port on an Arduino. If one attempts to use a software serial port, the Arduino will occasionally miss parsing characters and lock up the program. The Arduino MEGA has 4 hardware serial ports (only one other is used for USB communication), so this does not pose any problems.

2. One user noted about an issue with the doSBDRB() function. Code has been altered in accordance with this suggestion. See below for details:

“I found a bug in doSBDRB() when using a hardware serial port on the Mega 2560. When reading incoming data the for loop is not waiting for data to arrive. I was only getting the first 1 or 2 bytes written to the buffer I passed it. The rest was old data. I made the following changes and it seems to be working:”

This section of the doSBDRB() function in IridiumSBD.CPP now reads as follows. (Changes in bold).

for (int i=0; i= 1000UL * atTimeout)

return ISBD_SENDRECEIVE_TIMEOUT;

}

// if (stream.available())

// {

uint8_t c = stream.read();

if (rxBuffer && prxBufferSize)

if (*prxBufferSize > 0)

{

*rxBuffer++ = c;

(*prxBufferSize)–;

}

else

{

rxOverflow = true;

}

// }

// if (millis() – start >= 1000UL * atTimeout)

// return ISBD_SENDRECEIVE_TIMEOUT;

}

for (int i=0; size > i; ++i)

{

// wait for the data to come in

while (!stream.available())

{

if (cancelled())

return ISBD_CANCELLED;

if (millis() – start >= 1000UL * atTimeout)

return ISBD_SENDRECEIVE_TIMEOUT;

}

uint8_t c = stream.read();

if (rxBuffer && prxBufferSize)

if (*prxBufferSize > 0)

{

*rxBuffer++ = c;

(*prxBufferSize)–;

}

else

{

rxOverflow = true;

}

}

3. Another issue was found with the Pop-Up buoys when receiving messages. Two lines of code were missing at the end of the doSBDRB() function which are needed to process the “OK\r\n” string sent by the iridium module at the end of the iridium response.

After receiving a message, the iridium module will respond with

<<AT+SBDRB[size]____________[checksum]OK\r\n

However, the code only processed up to "…[checksum]". Issuing another command afterwards meant the "OK\r\n" was still in the stream buffer and would not process the next command properly.

This was solved by simply placing a waitForATResponse() after the checksum processes. (No parameters means it only looks for the terminator "OK\r\n").

This section of the doSBDRB() function in IridiumSBD.CPP now reads as follows. (Changes in bold).

uint16_t checksum = 256 * stream.read() + stream.read();

console(F("[csum:"));

console(checksum);

console(F("]"));

// Return actual size of returned buffer

if (prxBufferSize)

*prxBufferSize = (size_t)size;

console("\r\n"); //added this line to skip to next line in terminal

waitForATResponse(); //added this line to process "OK\r\n"

return rxOverflow ? ISBD_RX_OVERFLOW : ISBD_SUCCESS;

### 5.2.2. Software Serial

The updated software Serial library MUST be used for the pop-up buoy to function properly. It is saved as SoftwareSerial-PopUp.

The Pop-Up buoys use the Software Serial library to read and parse NMEA data from the GPS chip. The Software Serial buffer must be increased from 64 to 512 bytes to ensure no data is lost on long NMEA strings. This does use some extra RAM, but the ArduinoMEGA has plenty of reserve memory to accommodate this change. (Can be verified using the MemoryFree library). This is done by simply changing one line in the file SoftwareSerial.h :

#define _SS_MAX_RX_BUFF 512 // RX buffer size //BEFORE WAS 64

# 6. Program Flow

## 6.1. General Program Flow

A. Wake Up
B. Determine mode/phase based on current date/time and programmed cutoff dates/times

0 = Initial programming (before start date)

If mode = 0, display parameters and shut down after user removes USB, don’t take any sample data

1 = Bottom Sample

2 = Wait for Profile

3 = Under Ice

4 = Ice Free

C. Determine next sample time/date and set RTC alarm
D. Collect Sensor Data, Store to SD Card
E. If mode = 1 (Bottom Sample)

Do nothing else, just go to sleep

If mode = 2 (Wait for Profile)

Take initial depth measurement

Continuously take depth readings and compare to initial measurement

Wait for depth to change by m meters

Start profile

Collect profile data at 4 Hz for p seconds

Go to sleep

If mode = 3 (Under Ice)

**This mode is used primarily to preserve battery power if the is expected be under ice for several months after releasing from the bottom. In this mode the unit will only attempt to search for GPS once a day, rather than every hour.**

If hour = 15 (3pm, close to solar noon in most of Alaska)

Search for GPS for g seconds, n times, with delay in between

If GPS lock is found n times

Store GPS location and time on SD Card

Attempt to transmit iridium data

Else

Do nothing else, just go to sleep

If mode =4 (Ice Free)

4. Ice Free

Search for GPS for g seconds, n times, with delay in between

If GPS lock is found n times

Store GPS location and time on SD Card

Attempt to transmit iridium data

Else

Do nothing else, just go to sleep

## 6.2. Iridium Transmission

Once a GPS lock is found, the unit will attempt to transmit messages back via iridium SBD. Data is parsed from the SD Card and transmitted 100 characters at a time. The files are sent back in order of priority (profile data first, followed by under ice data, followed by pre-release bottom data). If the unit sends a message successfully, but then loses Iridium connection before sending all data (which happens often), it will go to sleep, but set the RTC to wake up the unit in 5 minutes, rather than the under ice sample interval. This 5 minute interval is used to get data back more quickly and take advantage of the calm sea state which is likely when the unit first surfaces. After all data is eventually sent, the unit will revert to sending its most recent GPS location and sample data once per day.

Each time the unit transmits a message, it will automatically check for any received messages. Received messages can tell the unit to change file, file position, or the interval of GPS location updates when all data is finished sending. Additionally, every time the unit wakes up and finds a GPS lock, the first message it attempts to send is “Hello!”. This is done in case any files are corrupted, causing the unit to lock up when sending data from the SD Card. In that case, the user may send a message to the unit, skipping to a different file location or file, and hopefully bypassing the corrupt data.

The SD Card will contain 2 files in addition to the data files: filepos.txt and summary.txt. The first unique message the unit attempts to send is summary.txt (simply a list of the files on the card and how long they are, to gauge how successful the unit was and how much data to expect. Filepos.txt is a single line text file used for the unit to remember how far along it is in the transmission process. Its format is “X,NNNNNNNNNNNNN”, where X indicates which file to open and NNNNNNNNNNNNN is the position to start reading the file (simply the number of characters after the start of the file). This is the exact same format for received messages. Values for X are as follows:

‘p’: “prodat.txt”

‘i’: “icedat.txt”

‘b’: “botdat.txt”

‘z’: if the file (or received message) starts with ‘z’, this should mean that the unit has completed sending all data and is now in sleep mode. NNNNNNNNNNNNN will indicate the interval, in seconds, for how long the unit will wait between sending updates on its most recent GPS location and sample data. By default, this is once per day.

## 6.3. Iridium Network - DITCO

# 7. Programming, Calibrating, and Testing the Units

## 7.1. Program (Sketch) Descriptions

Pop-Up Buoy uses 2 different programs, all described below. The Arduino IDE calls these different programs ‘sketches’.

Setup and Sensor Check (PopUp_5.3_SetupAndSensorCheck.ino)

This program is used during the assembly and testing phases to test that various sensors and utilities on the units are working properly. Once uploaded and the serial monitor is launched, the user is provided a status summary of the unit and a menu to check sensors and utilities one by one. If there are any problems that require changes such as re-connecting a sensor, it is usually necessary to close the serial monitor and re-upload the program. This will allow all sensors to initialize properly.

For details and instructions on using the Setup and Sensor Check Program, see the Pop-Up Buoy User’s Guide.

Deployment (PopUp_Deployment_5.3_Arduino_1.8.5.ino)

This program is used for deployments and calibrations. All deployment parameters (dates, sample intervals, etc.) must be manually entered into the program before uploading.

Once the program is uploaded and the serial monitor is launched, the user will be provided a long dialog confirming deployment parameters and verifying unit status. This dialog should be reviewed carefully for any possible errors.

For details and instructions on configuring units for deployment, see the Pop-Up Buoy User’s Guide.

## 7.2. Uploading Programs (Sketches)

To upload different programs to the Pop-Up Buoy, follow the steps below:

1. Connect all necessary sensors, antennas, coin cell batteries, and micro SD Card to unit electronics.
2. Connect unit to Power Supply (9V Battery or Power Supply with 9V, 1A with power on). Note: Do not use the main battery packs for testing or calibrating as it will deplete power necessary for the final deployment.
3. Connect unit to computer via USB cable
4. Open the Arduino IDE (Integrated Development Environment). Be sure to use version 1.8.5.
5. Open appropriate sketch
6. Select Board
  - Tools → Board → Arduino Mega 2650 or Mega ADK
7. Select COM Port
  - Check Device Manager → Ports to find correct port
  - Tools → Serial Port → COM__
8. Compile Sketch
  - Ctrl + R or Sketch → Verify/Compile
  - Should Read “Done Compiling” when complete
9. Upload Sketch
  - Ctrl + U or File → Upload
  - Should Read “Done Uploading” when complete
10. Launch Serial Monitor
  - Ctrl + Shift + M or Tools → Serial Monitor
  - Note: The baud rate should be set to 115200 (lower right-hand corner after launching Serial Monitor)
  - Note: 9V Power MUST be supplied and turned on before the serial monitor is launched. It is possible to upload sketches without external power, but power must be supplied for sensors to initialize properly when serial monitor is launched.
11. To upload a different sketch, close the serial monitor and begin at Step 5. It is not necessary to disconnect the unit from power or close the Arduino IDE.

## 7.3. Calibrating the Temperature Sensors

The data stored on the SD Card is a voltage reading from one of the unit’s ADC (Analog-to-Digital Converter). The voltage value is fit directly to a Steinhart-Hart curve during the calibration process so that no accuracy is lost by making conversions. Temperature can be calculated using the following equation:

T=1/(A+Blog_10 (x)+C[log_10 (x)]^3) - 273.15

Where:

T = Temperature in °C

x = ADC reading

A,B, and C = Steinhart-Hart Coefficients

The simplest way to program the unit to calibrate the temperature sensors is to use the deployment program and just have the unit take samples as if it were on the bottom waiting for release. Calibrations should always be done using a sample interval of 30 seconds – shorter sample intervals may cause small errors due to self-heating in the thermistor.

1. Follow procedures in section 6.1 to upload the sketch named PopUp_5.3_SetupAndSensorCheck.ino.
2. Set the RTC (Enter ‘2’ to set RTC time/date.) Ensure the RTC is synchronized with the clock on the temperature bath.
3. Check that RTC is keeping time (Enter ‘1’ – display Status)
4. Check that SD Card is connected and communicating properly (Enter ‘1’ – display Status)
5. Test the Thermistor probes to ensure it is connected and responding to temperature changes. A response should be visible just by holding the probe between 2 fingers.
6. Verify that the Temperature Reference is reading appropriate values. (Should be approximately 50 kOhms)
7. Close the Serial Monitor
8. Follow procedures in section 6.1 to upload the sketch named PopUp_Deployment_5.3_Arduino_1.8.5.ino
9. Set the value for BOTTOM_SAMPLE_INTERVAL to 30 seconds (within #define statements, line 42)
10. Set unitStart to an appropriate time in the near future
11. Set releaseTime to a time long after the calibration will be over. There is no risk of running out of storage space on the SD Card.
12. Compile the sketch (Ctrl + R or Sketch → Verify/Compile)
13. Upload the sketch (Ctrl + U or File → Upload)
14. Launch the Serial Monitor (Ctrl + Shift + M or Tools → Serial Monitor)
15. Carefully read the deployment dialog and verify all settings
16. Disconnect the unit from USB cable
17. Connect to 9V power (battery or power supply) before the unitStart time/date
  a. The unit can be temporarily disconnected from power as long as it is reconnected before the unitStart time/date. This way, multiple units can be connected and run off a single power supply for the calibration if desired.
18. Immerse temperature probes in temperature bath and start temperature bath program
19. Once temperature bath program has completed, download data from SD Card and process data
  a. Open a previous calibration file to see instructions and examples of how to process calibration data. Always use Paste Values.
    i. Download .CAL file from temperature bath computer
    ii. Follow numbered instructions on sheet TBxxxxx to process .CAL file
    iii. Format data from individual Pop-Up units and input into PopUpTempCal_xxx sheets. Follow numbered instructions and add new sheets if needed
    iv. Paste data into TempCalSummary Sheet and run genssh Macro for each unit
20. Record calibration coefficients. Store data and coefficients from temperature calibration for records and post processing data. (Data transmitted by the Pop-Up buoys is uncalibrated.)

## 7.4. Calibrating the PAR Sensor

The data stored on the SD Card is a voltage reading from one of the unit’s ADC (Analog-to-Digital Converter). The PAR Sensor is a photodiode which outputs a small current which is proportional to the amount of light hitting the sensor. The sensors are calibrated by the manufacturer and provide a known current output vs. incoming PAR.

PAR can be calculated using the following equation:

PAR=(y-y_0 )*0.000668268/m*1/0.73

Where:

PAR = Photosynthetically active radiation (in µmolm⁻²s⁻¹)

y = ADC reading

y0 = ADC reading at 0 µmolm⁻²s⁻¹

m = calibration from manufacturer (uA/µmolm⁻²s⁻¹)

0.000668268 is a fixed conversion factor for the circuit which converts voltage to current. Details on this can be found in the document PAR circuit calculations - Rev 5.3.xlsx.

0.73 is a scaling factor to account for the amount of light that is absorbed/reflected by the acrylic housing. This was found experimentally by comparing a calibrated Satlantic PAR sensor to several Pop-Up buoy PARs mounted together and exposed to identical light conditions.

The only factor that must be calibrated is y0. This is found by exposing the sensor to zero light and measuring the response. This is most easily done by using the SetupandSensorCheck sketch and recording the response from the PAR sensor with the end cap placed upside down on a black surface (no incoming light).

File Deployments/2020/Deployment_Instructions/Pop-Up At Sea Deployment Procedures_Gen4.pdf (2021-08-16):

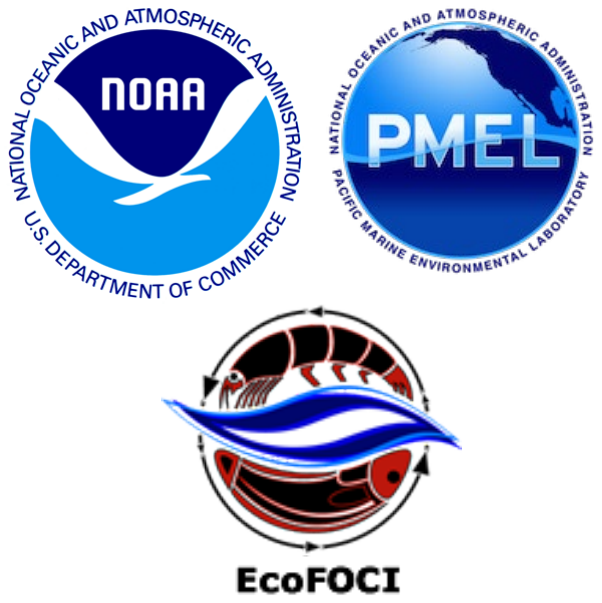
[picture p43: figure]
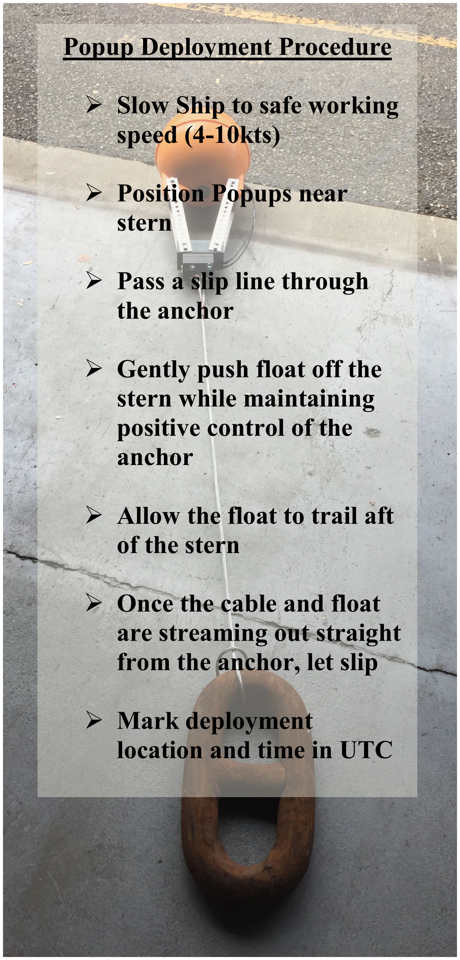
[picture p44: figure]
Popup Deployment Procedure; Slow Ship to safe working speed (4-10kts); Position Popups near stern; Pass a slip line through the anchor; Gently push float off the stern while maintaining positive control of the anchor; Allow the float to trail aft of the stern; Once the cable and float are streaming out straight from the anchor, let slip; Mark deployment location and time in UTC

POPUP GEN. 4
DEPLOYMENT PROCEDURES
SUMMER / FALL 2019

Point of Contact
LTJG Sarah Donohoe
sarah.s.donohoe@noaa.gov
office 206-526-6746
Background
The Popup buoys are one of several new technologies in development by the Innovative Technology for Arctic Exploration (ITAE) grant. They are compact instruments housed in low-cost commercial crab floats and optimized for use in the relatively shallow waters of the Arctic continental shelf. The buoys are expendable and capable of providing approximately 18 months of data transmitted via Iridium shortburst-data messages; designed to be sunk with an anchor and a timed burn-wire release at sea during late summer to early fall in ice-free conditions. At a preprogrammed release date the burn wire will release the anchor and the sensors will capture a single water column profile as it rises and gets trapped under the ice. In this phase the Popup collects oceanographic data on conditions directly under Arctic sea ice during spring and early summer. Once the Arctic sea ice retreats and the float is freed the Popup begins transmitting stored data and location until battery life is fully drained.

Popup Prep: 1 day prior to Deployment
1) Pump Vacuum to -10psi
a) Remove the vacuum cap plug (marked
by arrows) with pliers. Keep in mind the O-ring on this plug must be kept clean and free of dust or debris. It is the only thing keeping water from entering the valve and flooding the Popup.
b) Attach the hand-pump hose. The valve attachment on the hose should twist ¼
turn clockwise and lock in place. Use
pliers to turn the valve attachment if your

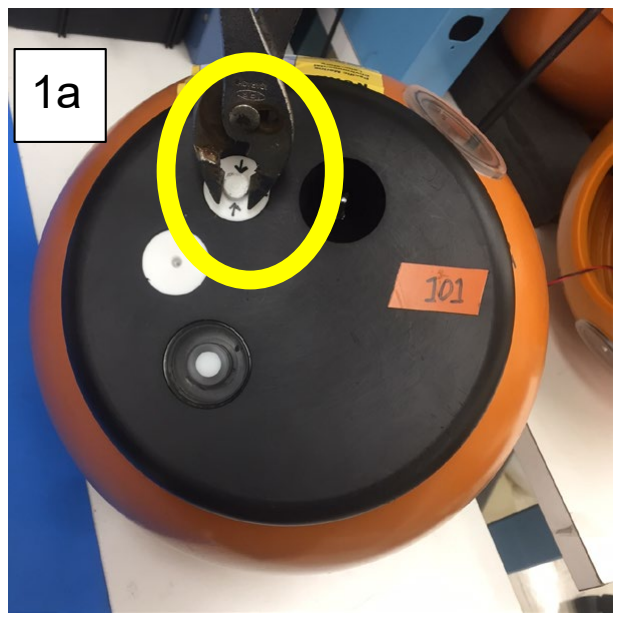
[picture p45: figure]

fingers don’t fit in the cutout. PLEASE NOTE THE VALUE IN PSI OF THE
VACUUM YOU SEE ON THE GUAGE: IF THE VACUUM IS AT OR BELOW -
6 PSI PLEASE DO NOT DEPLOY. **Please write down vacuum pressure before pumping on deployment sheet.
c) Pump air out until gauge reads -10psi. Be sure the switch at the hand pump nozzle is set to vacuum (not pressure). This may take ~100 squeezes.
**Please write down vacuum pressure after pumping on deployment sheet.
d) Clean the vacuum cap plug and mating surface on the float. Re-grease O-ring if necessary. Replace plug. To replace the plug, you can use pliers to push down until the lower surface of the plug top is below the black end cap surface. The cap has to be pushed down hard to displace air with a plunging motion.

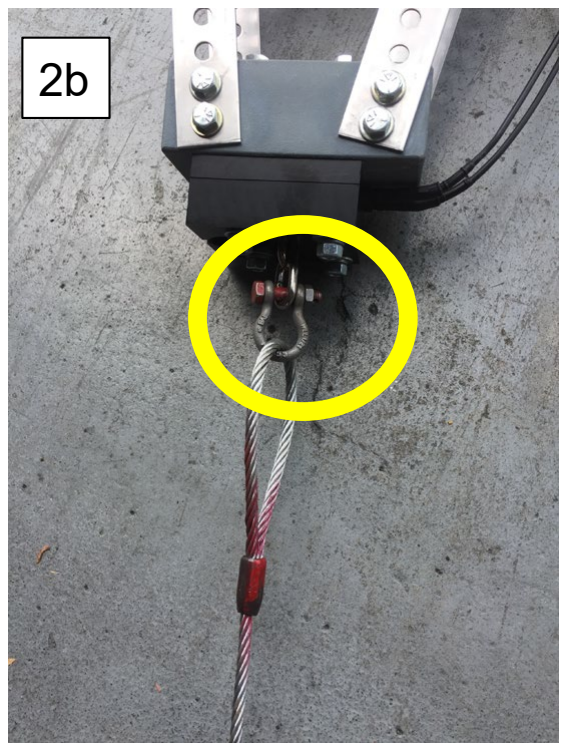
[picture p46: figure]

2) Attach Anchor
a) Loop the anchor cable around the
anchor chain link and back through the
cable eye in a hitch

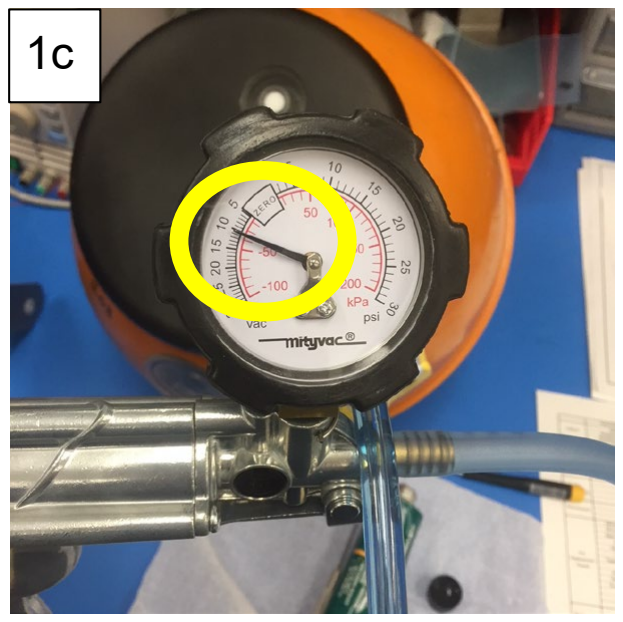
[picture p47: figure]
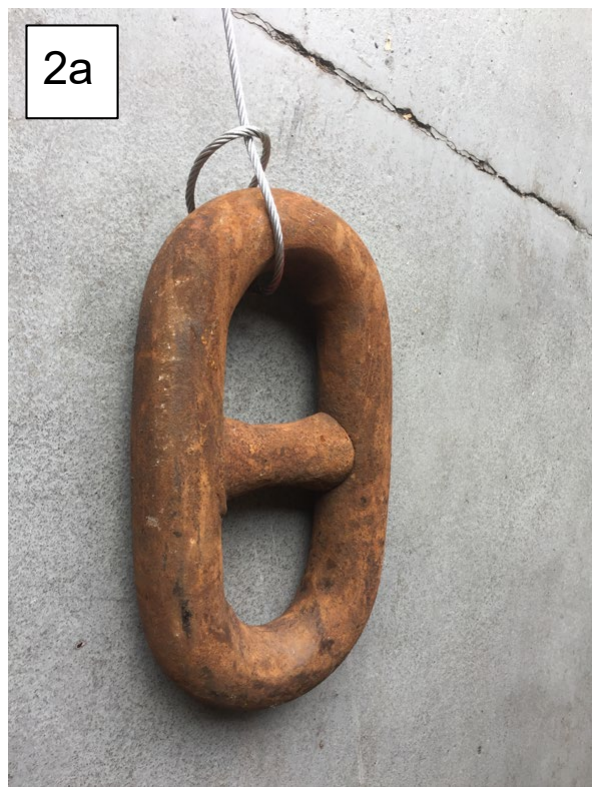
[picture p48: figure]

b) Attach the free end of the cable to the lower chain link on the release block via the shackle. Use a cotter pin to secure shackle.

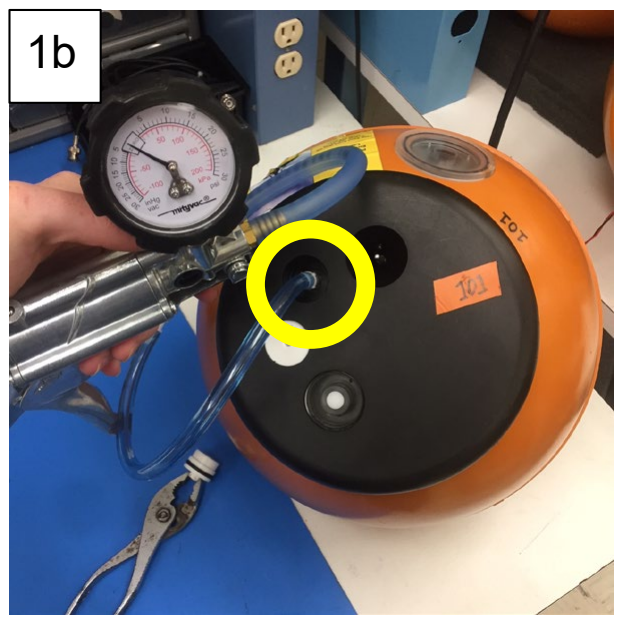
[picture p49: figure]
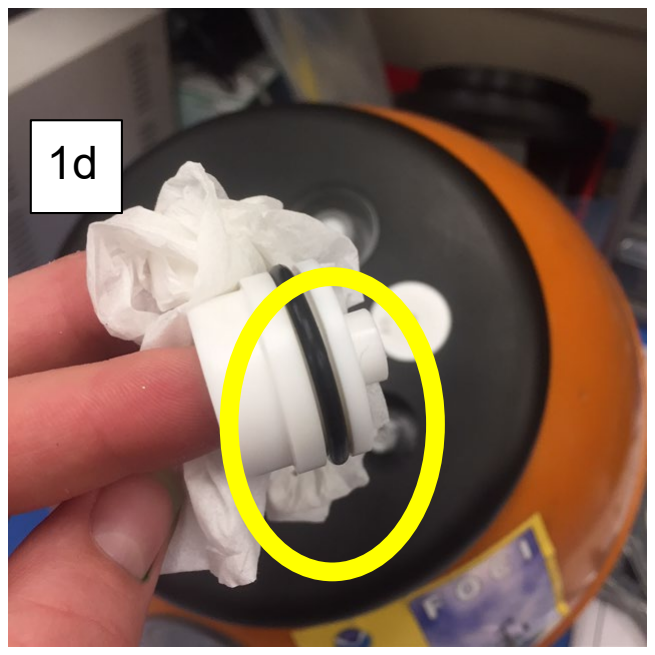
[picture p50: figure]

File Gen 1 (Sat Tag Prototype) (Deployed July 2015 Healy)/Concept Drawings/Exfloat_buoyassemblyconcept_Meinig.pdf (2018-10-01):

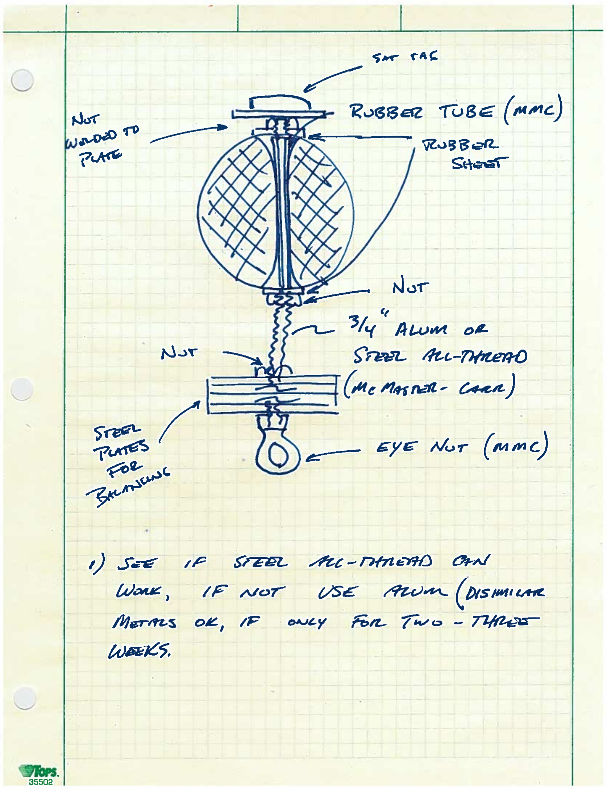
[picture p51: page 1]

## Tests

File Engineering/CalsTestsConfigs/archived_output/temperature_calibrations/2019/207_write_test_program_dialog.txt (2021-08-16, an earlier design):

Unit Status:
  SD Card Initialized Successfully.
  Current RTC Time/Date: Jun 06 2019 18:39:40
  Temp Sensor ADC Val: 9340 (approx 13.14 C)
  SST (Sea Surface Temp) Sensor ADC Val: 9463 (approx 12.86 C)
  Temp Ref    ADC Val: 8516 (approx 15.54 kOhms)
  PAR  Sensor ADC Val: 5464 (approx 0.26 umol/(m2s))
  Fluorometer ADC Val: -467 (approx ? ug/L)
  100m Pressure Sensor Val: 18171 (approx 5.45 m)
  Tilt Angle: 177 degrees from horizontal

Deployment Schedule:
--PHASE 1 (ON BOTTOM)--
 -This mode starts at the scheduled Start Time.
  Unit will start sampling [Jun 06 2019 18:50:00] and take a sample every (0h,0m,30s)
--PHASES 2 AND 3 (WAIT FOR AND COLLECT PROFILE)--
 -This mode starts just before the scheduled Release Time.
  Release Expected [Jun 04 2020 17:00:00] (<--Set Burn Wire Release for this exact time/date.)
  Unit will wake up  (2h,0m,0s) before scheduled release and wait for profile.
  Start of profile will be triggered by a change in depth of (2 meters).
  Profile will sample at 4 Hz for (0h,1m,30s) seconds before proceeding to phase 3. 
  If unit does not sense the release within  (4h,0m,0s) of waking it will assume it missed the profile and proceed to phase 3.
--PHASES 4 AND 5 (UNDER ICE AND TRANSMIT DATA)--
 -This mode starts after profile has been collected (or missed).
  Unit will take a sample every (1h,0m,0s) and take an image once a day.
  Unit will search for GPS satellites for (0h,2m,0s)  after every sample.
  If unit does successfully find a GPS satellite, it will attempt to send all collected data back in the following order:
    1-File Summary, 2-Profile Data, 3-Under Ice Data, 4-Bottom Data, 5-Daily Images
  If any iridium messages send successfully, it will continue sending until one message fails and make the next attempt to send in (0h,20m,0s)
  Otherwise, if no messages send, the unit will take the next sample and attempt to send again in (1h,0m,0s)
--PHASE 6 (SURFACE DRIFTER)--
 -This mode starts after all data has finished sending.
  Unit will take a sample every (3h,0m,0s) and search for a GPS fix for (0h,2m,0s) after every sample.
  Unit will attempt to send any new data regardless of whether a GPS fix was found

**Check all settings, take a screenshot of this dialog, and disconnect from USB when ready.**
**Set Burn Wire Release for [Jun 04 2020 17:00:00]**

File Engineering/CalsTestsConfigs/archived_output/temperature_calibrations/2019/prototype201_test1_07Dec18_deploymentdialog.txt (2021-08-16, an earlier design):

Unit Status:
  SD Card Initialized Successfully.
  Current RTC Time/Date: Dec 07 2018 11:41:22
  Temp Sensor ADC Val: 9602 (approx 12.55 C)
  SST (Sea Surface Temp) Sensor ADC Val: 32767 (approx -11.49 C)
  Temp Ref    ADC Val: 8488 (approx 15.49 kOhms)
  PAR  Sensor ADC Val: 5460 (approx 0.00 umol/(m2s))
  Fluorometer ADC Val: -472 (approx ? ug/L)
  100m Pressure Sensor Val: 16467 (approx 0.25 m)
  Tilt Angle: 178 degrees from horizontal

Deployment Schedule:
--PHASE 1 (ON BOTTOM)--
 -This mode starts at the scheduled Start Time.
  Unit will start sampling [Dec 07 2018 15:00:00] and take a sample every (1h,0m,0s)
--PHASES 2 AND 3 (WAIT FOR AND COLLECT PROFILE)--
 -This mode starts just before the scheduled Release Time.
  Release Expected [Dec 11 2018 09:00:00] (<--Set Burn Wire Release for this exact time/date.)
  Unit will wake up  (2h,0m,0s) before scheduled release and wait for profile.
  Start of profile will be triggered by a change in depth of (2 meters).
  Profile will sample at 4 Hz for (0h,1m,30s) seconds before proceeding to phase 3. 
  If unit does not sense the release within  (4h,0m,0s) of waking it will assume it missed the profile and proceed to phase 3.
--PHASES 4 AND 5 (UNDER ICE AND TRANSMIT DATA)--
 -This mode starts after profile has been collected (or missed).
  Unit will take a sample every (1h,0m,0s) and take an image once a day.
  Unit will search for GPS satellites for (0h,0m,20s)  after every sample.
  If unit does successfully find a GPS satellite, it will attempt to send all collected data back in the following order:
    1-File Summary, 2-Profile Data, 3-Under Ice Data, 4-Bottom Data, 5-Daily Images
  If any iridium messages send successfully, it will continue sending until one message fails and make the next attempt to send in (0h,20m,0s)
  Otherwise, if no messages send, the unit will take the next sample and attempt to send again in (1h,0m,0s)
--PHASE 6 (SURFACE DRIFTER)--
 -This mode starts after all data has finished sending.
  Unit will take a sample every (3h,0m,0s) and search for a GPS fix for (0h,2m,0s) after every sample.
  Unit will attempt to send any new data regardless of whether a GPS fix was found

**Check all settings, take a screenshot of this dialog, and disconnect from USB when ready.**
**Set Burn Wire Release for [Dec 11 2018 09:00:00]**

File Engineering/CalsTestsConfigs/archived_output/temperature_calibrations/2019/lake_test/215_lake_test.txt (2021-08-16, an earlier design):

Unit Status:
  SD Card Initialized Successfully.
  Current RTC Time/Date: Jul 11 2019 20:49:20
  Temp Sensor ADC Val: 9600 (approx 12.56 C)
  SST (Sea Surface Temp) Sensor ADC Val: 32767 (approx -11.49 C)
  Temp Ref    ADC Val: 8508 (approx 15.53 kOhms)
  PAR  Sensor ADC Val: 5466 (approx 0.39 umol/(m2s))
  Fluorometer ADC Val: -433 (approx ? ug/L)
  100m Pressure Sensor Val: 16464 (approx 0.24 m)
  Tilt Angle: 178 degrees from horizontal

Deployment Schedule:
--PHASE 1 (ON BOTTOM)--
 -This mode starts at the scheduled Start Time.
  Unit will start sampling [Jul 11 2019 23:00:00] and take a sample every (1h,0m,0s)
--PHASES 2 AND 3 (WAIT FOR AND COLLECT PROFILE)--
 -This mode starts just before the scheduled Release Time.
  Release Expected [Jul 15 2019 17:00:00] (<--Set Burn Wire Release for this exact time/date.)
  Unit will wake up  (2h,0m,0s) before scheduled release and wait for profile.
  Start of profile will be triggered by a change in depth of (1 meters).
  Profile will sample at 4 Hz for (0h,1m,30s) seconds before proceeding to phase 3. 
  If unit does not sense the release within  (4h,0m,0s) of waking it will assume it missed the profile and proceed to phase 3.
--PHASES 4 AND 5 (UNDER ICE AND TRANSMIT DATA)--
 -This mode starts after profile has been collected (or missed).
  Unit will take a sample every (1h,0m,0s) and take an image once a day.
  Unit will search for GPS satellites for (0h,2m,0s)  after every sample.
  If unit does successfully find a GPS satellite, it will attempt to send all collected data back in the following order:
    1-File Summary, 2-Profile Data, 3-Under Ice Data, 4-Bottom Data, 5-Daily Images
  If any iridium messages send successfully, it will continue sending until one message fails and make the next attempt to send in (0h,20m,0s)
  Otherwise, if no messages send, the unit will take the next sample and attempt to send again in (1h,0m,0s)
--PHASE 6 (SURFACE DRIFTER)--
 -This mode starts after all data has finished sending.
  Unit will take a sample every (3h,0m,0s) and search for a GPS fix for (0h,2m,0s) after every sample.
  Unit will attempt to send any new data regardless of whether a GPS fix was found

**Check all settings, take a screenshot of this dialog, and disconnect from USB when ready.**
**Set Burn Wire Release for [Jul 15 2019 17:00:00]**

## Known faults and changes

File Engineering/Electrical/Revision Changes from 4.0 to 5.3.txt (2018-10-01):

REV 5.0:
-Two U22s listed on Rev 4.0 BOM.  Changed LT1634 to U23 to match schematic

-R4/C25 and U22/C26 were connected to +5V instead of +5V_SP.  Changed and rerouted so all are on proper net

-Connected U5/C6/R10 to +3V3_SP instead of +3V3 

-Tied Wake Up function of RTC and inverter to primary battery instead of coin cell
-Added R29 to schematic to lower Alarm function to proper voltage (simple resistor divider)
-Added R29 to BOM

-Changed R1,R2,R3 Values for Better PAR Sensitivity (Done by hand on First build, no software changes needed)
-Now R1=137k, R2=10k, R3=2k
-Changed BOM for R1,R2,R3

-Changed R4, R6, R12, TR1 Values for Better Temperature Sensitivity (Same as MTRDuino Version 5.2)
-Now R4=200k, R6=324k, R12=50k, TR1=50k
-Changed Size of R4 and R6 to 1206
-Changed Size of R12 to 2010
-Changed BOM for R4, R6, R12, TR1
-Changed ADC Gain Settings on Software to Gain of 4

-Changed C1-C5 Values
-Changed BOM to reflect C1-C5 changes

-Changed IridiumTX and RX to Arduino Hardware pins
-Verified Wiring
-Routed Iridium TX and RX lines
-Re-Routed 3.3V Sensor Power On Signal (Arduino MEGA Pin 22)

-Changed D2,D3 to Shottky Diode
-Changed BOM for D2,D3

-Removed Second Pressure Sensor header
-Removed J3, JP3 from BOM

-Changed (JP5) GPS Antenna Jack from Right Angle to Vertical
-Changed BOM for J5

-Added JP7 - 3x2 header for Turner Cyclops fluorometer probe
-Added U24 - ADS100-A2 ADC for fluorometer probe
-Added U25 - Dual SPST switch for fluorometer sensitivity control
-Added JP7, U24, U25 to BOM
-Connected pins 24 and 26 of Arduino MEGA to U25
-Added R13, R14 as current limiting resistors for pins 24 and 26
-Added R13,R14 to BOM
++Need to check code to control fluorometer and test sensitivity

-Changed BOM for micro fit 3 headers to press fit ()

-Changed U16 (microSD Card slot) to P/N: 3M5607CT-ND  (Old part obsolete)
-Disconnected GND1 and GND3 pins on U16 - new part
-Changed U16 (microSD Card) on BOM

-------------------------------------------------------------------------------------------------
REV 5.1:
-Added PicoBlade Connector for rockblock 9603
-Removed Rockblock 9602 from BOM
-Added RockBlock9603 to BOM
-Added picoblade Connector to BOM

-Changed 3.3V Sensor Power to pin 32
-Changed pin assignment in software

-Changed Iridium on/off to pin 11
-Changed pin assignment in software

-Changed Iridium power to pin 8
-Changed pin assignment in software

-Added separate On/Off switch for Fluorometer (Pin 28)
-Added pin assignment in software
**Need to add fluorometer power function to software
-Added R15, R16, Q7
-Added R15, R16, Q7 to BOM

-Changed GPS to Hardware Serial
++Need to check gps change to hardware serial in code
-Removed C12 and U11 from BOM

-Added U26 for 3 hardware serial devices for voltage translation
-Added U26, C28, C29 to BOM
-Added code to turn on Serial Comms on startup

-Added power switch for UCAM-III (Pin 12)
-Added R30,R31,Q8 to BOM

-Added reset switch for UCAM-III to (Pin 13)
-Added R32 to BOM

-Removed GPS Serial Test points
-Removed 4 TPs from BOM

-Added R33: 10k current limiting resistor from MTR/MTRDuino Temp Circuit
-Added R33 to BOM

-Changed Temp circuit to incorporate SST Probe
-Changed U7 to DG2034E
-Added R34, JP3
-Added TEMP2 Control switch to Pin 4 of Arduino
-Removed U5, C6, R10
++Need to check software for temp selection

-Removed file.available so code doesn't overflow if size is larger than an int

++Need to check SBD message format, include file as first 2 bytes, filepos as next 4 bytes

++Need to check image ordering and timing 

**Timeout or error handling for camera??????

**Add code for SST drifter mode

**Check failsafe for alarm wakeups if transmitting data

**Need to adjust Accel code for horizontal PCB

-------------------------------------------------------------------------------------------------
REV 5.2:
- Reversed Pins for JP8 (Iridium header) to fit pre-made PicoBlade Assembly (pin 10 on header A onnects to pin 1 on header B on pre-made assemblies)
- Re-routed pins for JP8 

- Re-routed input pins to U25 (Switch inputs IN1 and IN2 and common inputs COM1 and COM2 were backwards)

TEMPERATURE SENSOR SWITCH IMPLEMENTED IN REV 5.1 DID NOT WORK
  -Removed R33 (current limiting 10k resistor  on temp circuit)
  -Removed R33 from BOM
  -Removed R34 (49.9k resistor on temp circuit)
  -Removed R34 from BOM
  -Replaced U7 with ADG836
  -Changed U7 on BOM
  -Added U5,C6,R10 (NL17SZ07 to translate temp switch level from 5V to 3.3V)
  -Added U5,C6,R10 to BOM
  -Added U11,C12 (MAX4624 to switch between top temp and SST probes)
  -Added U11,C12 to BOM
-------------------------------------------------------------------------------------------------
REV 5.3
IRIDIUM SERIAL COMMSN IN REV 5.2 DID NOT WORK
  - Disconnected Iridium Serial lines from Voltage Translator
  - Rerouted Iridium Serial Comms directly from Arduino to Iridium Header

Connected U5 and U8 to 3.3V/3.3V_SP instead of 5V/5V_SP 
  - Rerouted power lines for these

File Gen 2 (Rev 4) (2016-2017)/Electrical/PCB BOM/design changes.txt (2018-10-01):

-Add 10k Pull up resistor to U5 and U11 outputs (NL17SZ07 is open drain, cannot pull high)
    - R8 and R10
	
**SPI Mode 0 or 2 for SD card?

-Changed to microfit 3.0 connectors

- Moved placement of iridium module
	- Moved other components to fit better
	
- Swapped Pins A14 and A15 for Iridium TXD and RXD

- Changed Pin 44 to Pin A6

- Changed Pin 8 to Pin 22

- Changed Pin 22 to Pin 8

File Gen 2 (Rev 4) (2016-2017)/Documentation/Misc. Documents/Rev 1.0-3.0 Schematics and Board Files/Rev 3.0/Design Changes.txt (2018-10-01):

Labeled R5,7,9,11 properly with 3.74K

Renamed U10 to JP3

Renamed D1 to JP0

Labeled C3 properly as 0.1 uF

Added JP5 and J5 to BOM (header and connector for thermistor)

Labeled/named U21 properly (LT1129 5v regulator)

Changed U5 from M74VHC1GT125 to NL17SZ07DFT2G (Used wrong IC for 5V to 3v3 logic shift)

Changed Test Point size to 0.040"

Changed Test Points to Red, Black, and Yellow

Updated BOM for temp circuit resistors - R12,15,16,13 (switched package sizes)

Routed Pin 3 to +5V on U18 (3v3 regulator ENABLE wasn't connected)

Changed C3 to VDD input of U2, Temperature ADC (Was connected to Vin-)

Changed NPN transistors (T1-T4) to PNP Transistors (Q3-Q6)

Changed headers for all sensors to Molex 70543

Moved Iridium to Bottom of PCB

Changed Iridium Power and Iridium OnOff Pins

Added logic gate to adxl345 SPI lines

Added Diode to Arduino +5V

Changed temperature circuit

Changed BOM for temp circuit

*Use taller female headers for Arduino ICSP and Iridium Module

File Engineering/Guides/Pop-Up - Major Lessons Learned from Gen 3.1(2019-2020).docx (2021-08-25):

# Pop-Up Major Lessons Learned from Gen 3.1

- PAY ATTENTION TO TIME TO FIRST FIX**Main draw on power budget was searching for GPS fix (~60% of total power budget in worst case scenario)** Software changed to search for a single GPS satellite instead of a full fix (requires only a few seconds vs. several minutes)** …From “Major Lessons Learned from Gen 2”

LESSON LEARNED:

https://www.lifewire.com/time-to-first-fix-ttff-1683313

“If a GPS device is new, has been turned off for a long period of time, or has been transported for a long distance since it was last turned on, it will take longer to acquire these data sets and get a Time to First Fix. This is because the GPS data is outdated and needs to download up-to date information.”

For Gen 3 buoys deployed in 2018 (3800, 1240, 5210, 8220) the software was changed to search for a single fix, and the timeframe to find a fix before going back to sleep mode was set for 20 seconds. We found that floats 5210 and 8200 had errors sending back surface drifter GPS coordinates at the time of sampling because they struggled to acquire first fix… we still recovered Iridium coordinates (albeit less accurate than the onboard GPS), and the drifter function of the float is seen as accessory. All data was transmitted successfully. However, for Gen 3.1 and 3.2 the software was changed to look for a single satellite for 2 minutes, after which, if unsuccessful, the unit would return to its sleep mode.

- STILL LOOKING FOR BEST MECHANICAL RELEASE SOLUTION (Another!) new burn wire developed by DBV Technology : Release Block. New design houses circuit board controller and battery pack for burn wire inside the trawl float housing. A brass 7/16-20 bulkhead penetrator provides through-hull connection from battery pack and release board to the release wire.

LESSON LEARNED:

DBV tech was extremely difficult to work with, there was poor communication from Bud Vincent throughout the design and purchasing process. Originally he told me that the new design would result in a $250-$275 per unit cost, final price was $585 per unit (still a reduction from the self-contained cylinder, which cost $750 each). Furthermore, at sea the potting that bound to the penetrator on pop-up SN 211 or 215 separated. Would not recommend using DBV tech for partnerships in the future.

- CIRCUIT BOARD QUIESCENCE, ADDED REGULATOR

See EcoFOCI_PopUp>Engineering>Electrical>Voltage Regulator Mod

Boards were short-circuiting regularly, Dirk Tagawa identified this regulator modification as a fix.

- OVERBALLASTED, AND RELEASE DATE IN LATE OCTOBER IN BERING SEA RESULTING IN INCOMPLETE DATA TRANSFER

THE DBV tech cable that reached from the float to the release block was too short, so we shortened the frame to accommodate it and reduced the righting moment arm. Data return was very spotty on these units, rough weather in the Bering Sea in late October and a heavier build with a shorter frame resulted in interrupted data streams. Salt water interrupts the Iridium data transmission, the floats sent lots of short “Hello” messages and ran their battery down trying to connect with satellite at the surface but not connecting for long enough to transmit data. These floats had just 2.5” of freeboard, compared with Gen 3 which had 3.5” of freeboard. Despite successful lake tests, data transmission was spotty in the field. One thing to note is that Iridium satellite data transmission can occur through small layers of freshwater, but not at all through salt water. Word of caution for future testing in lake for marine field equipment.

- ISSUES WITH VACCUUM HOLDING AT THE SST THERMISTOR PROBE, CHANGED TAPERED THREAD TO SAE ORB

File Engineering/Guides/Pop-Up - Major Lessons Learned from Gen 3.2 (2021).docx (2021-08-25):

# Pop-Up Major Lessons Learned from Gen 3.2

- LENGTHENED DBV TECH CABLE
- REPLACED STEEL BALLAST RELEASE MOUNT WITH PURPLEHEART WOOD
- REPLACED TAPERED THREAD SST WITH SAE-ORB THERMISTOR HOUSING, MUCH MORE RELIABLE VACUUM!

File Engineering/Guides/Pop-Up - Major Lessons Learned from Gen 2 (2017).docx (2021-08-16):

# Pop-Up Major Lessons Learned from Gen 2

# 1. Lessons Learned from Gen 2

-Major operational limitation was 170 day limit on burn wire release

-New burn wire developed by DBV Technology

- Higher load limit reduces need for a load reducing mechanism; cost savings from machined parts is equivalent to the additional cost of improved burn wire mechanism

-Pressure Data from Gen 2 showed that 10 bar and 3 bar pressure sensors were always within 2 cm of each other

-3 bar pressure sensor not needed – removed entirely from Gen 3

-Buoys ascended at approximately 1m/s when profiling with minimum buoyancy required for successful data transmission

**Sea anchor likely needed to be added to slow buoy during ascent-not yet tested or integrated

-Temperature Probe changed to thinner style to reduce ‘temperature lag’ when profiling. Small hole also drilled in side of end cap to improve water flow past probe tip when profiling

-Sea Surface Temperature (SST) could be very desirable and allow for possible funding from NWS because buoys surface at times and locations with very few SST reporting stations. Buoys also worked remarkably well in moderate to high sea state (25-30 kts, 5-8 ft seas)

-SST Probe added to bottom of float

**SST reporting requirements should be investigated and collaboration with NWS should take place to acquire possible funding

-Large number of machined parts (17) added undesirable costs to production

-Number of machined parts reduced from 17 to 8 in favor of off the shelf components and simpler components (such as PCB Mount)

-Temp, Depth, and PAR Data looked great, but more sensors needed for science purposes

-Integrated optional fluorometer

-Integrated small camera for situational awareness

**Cost of fluorometer is still quite high (~$1,500). Opportunities should be explored in the future for developing a low-cost fluorometer

-GPS time comparison showed very little drift in buoys internal clocks (<<1 minute in 6 months).

-Time very reliable for synchronizing with any independent release mechanism

-Main draw on power budget was searching for GPS fix (~60% of total power budget in worst case scenario)

-Software changed to search for a single GPS satellite instead of a full fix (requires only a few seconds vs. several minutes)

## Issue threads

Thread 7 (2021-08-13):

### ISSUE TITLE
Add Flag or Switch to determine if image code needs to run or not

### ISSUE THREAD

**Issue by shaunwbell** [NOAA-PMEL/EcoFOCI_PopUp#7]
not all popups have camera's and when a popup doesn't have a camera... a large 4gb mythical file gets created (so try to prevent this)

**Comment by sarahsdonohoe** [comment]
we didn't prevent the file from getting created, but as a workaround we added a line that will delete the placeholder image file if it's created

**Comment by sarahsdonohoe** [comment]
we didn't prevent the file from getting created, but as a workaround we added a line that will delete the placeholder image file if it's created

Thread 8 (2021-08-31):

### ISSUE TITLE
Keep working-overhaul branch separate from main branch for now

### ISSUE THREAD

**Issue by sarahsdonohoe** [NOAA-PMEL/EcoFOCI_PopUp#8]
Everything currently in the main branch is under "archive" in the working-overhaul branch. However, all the information in main is re-organized into different folders broken down by deployment year. Engineering folder in working-overhaul reflects only the most recent builds (Generation 3.2), and archives of engineering folders should be kept for Generations 1, 2 and 3 in the archive folder.  Generations 3, 3.1 and 3.2 are nearly identical in programming. The largest difference is frame design and the circuit board regulator modification.

**Comment by shaunwbell** [comment]
RENAMED overhaul to master and archived older master as another archive.  everyone will want to re download their versions

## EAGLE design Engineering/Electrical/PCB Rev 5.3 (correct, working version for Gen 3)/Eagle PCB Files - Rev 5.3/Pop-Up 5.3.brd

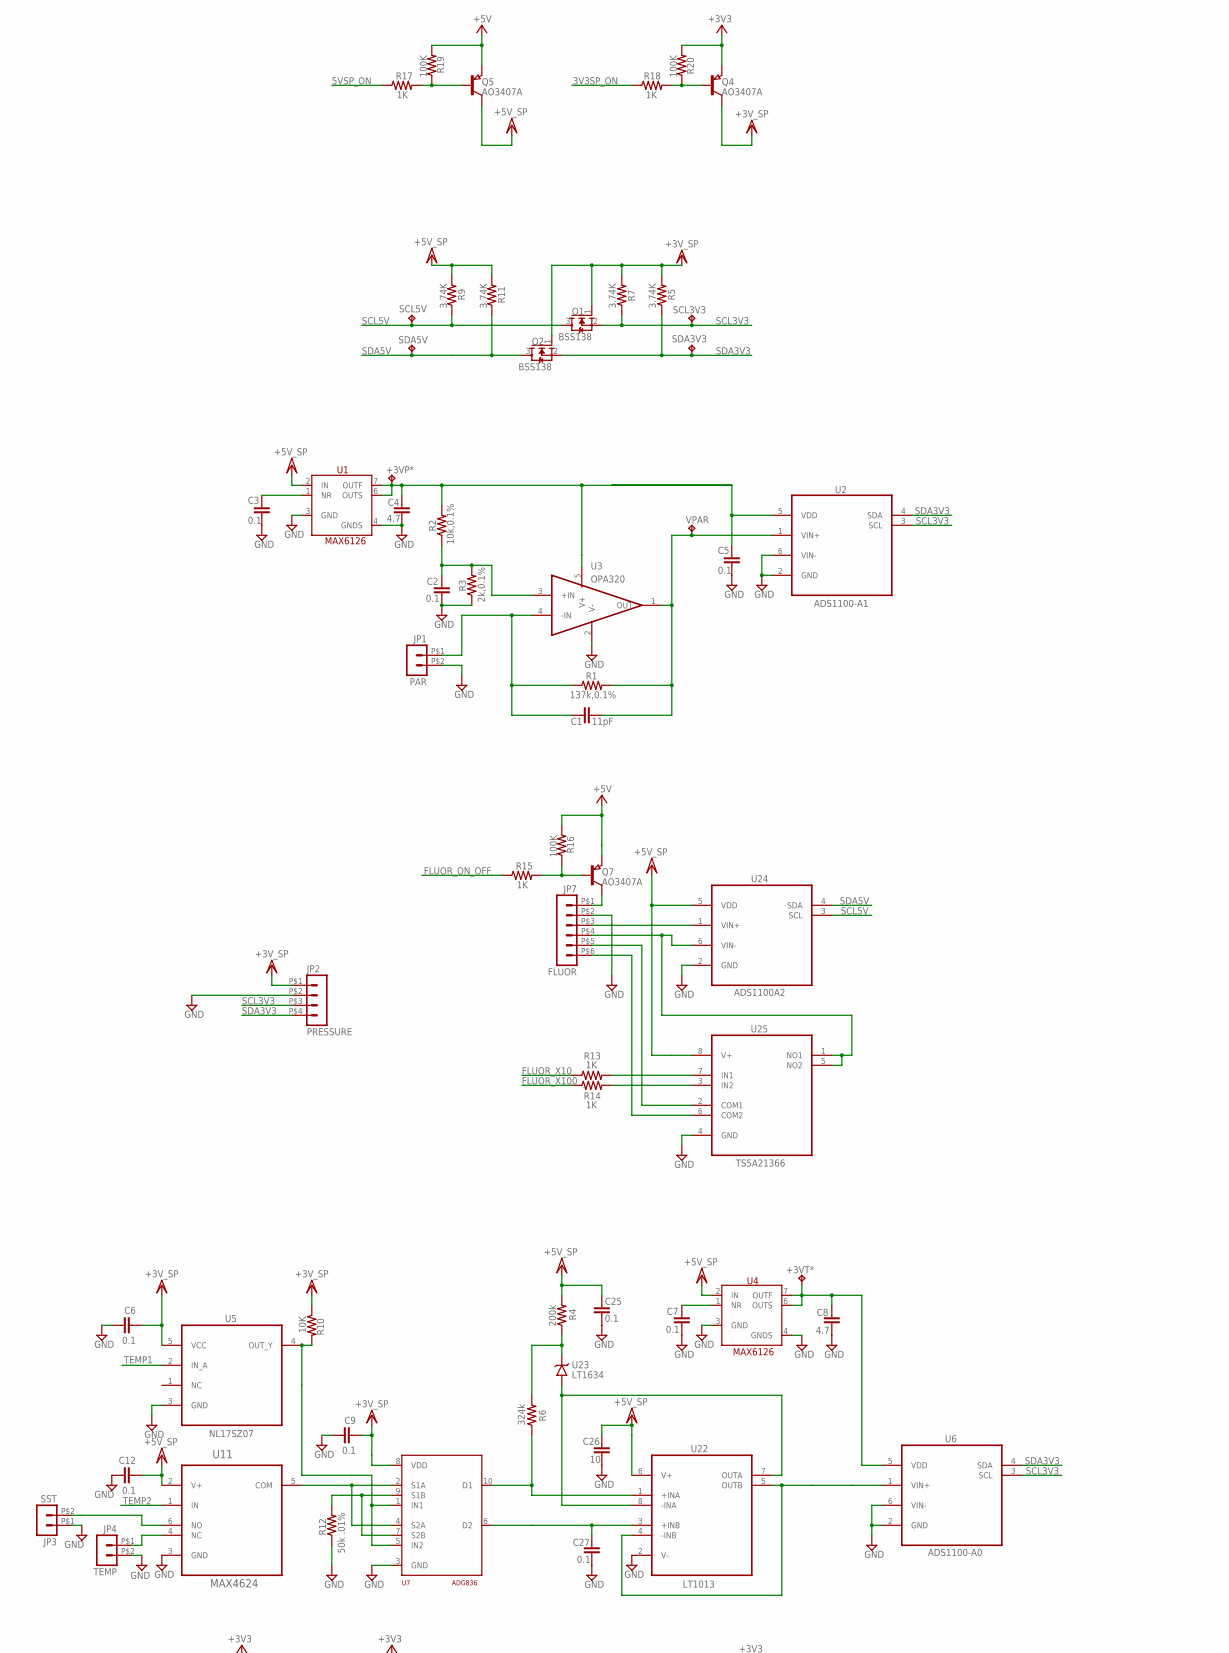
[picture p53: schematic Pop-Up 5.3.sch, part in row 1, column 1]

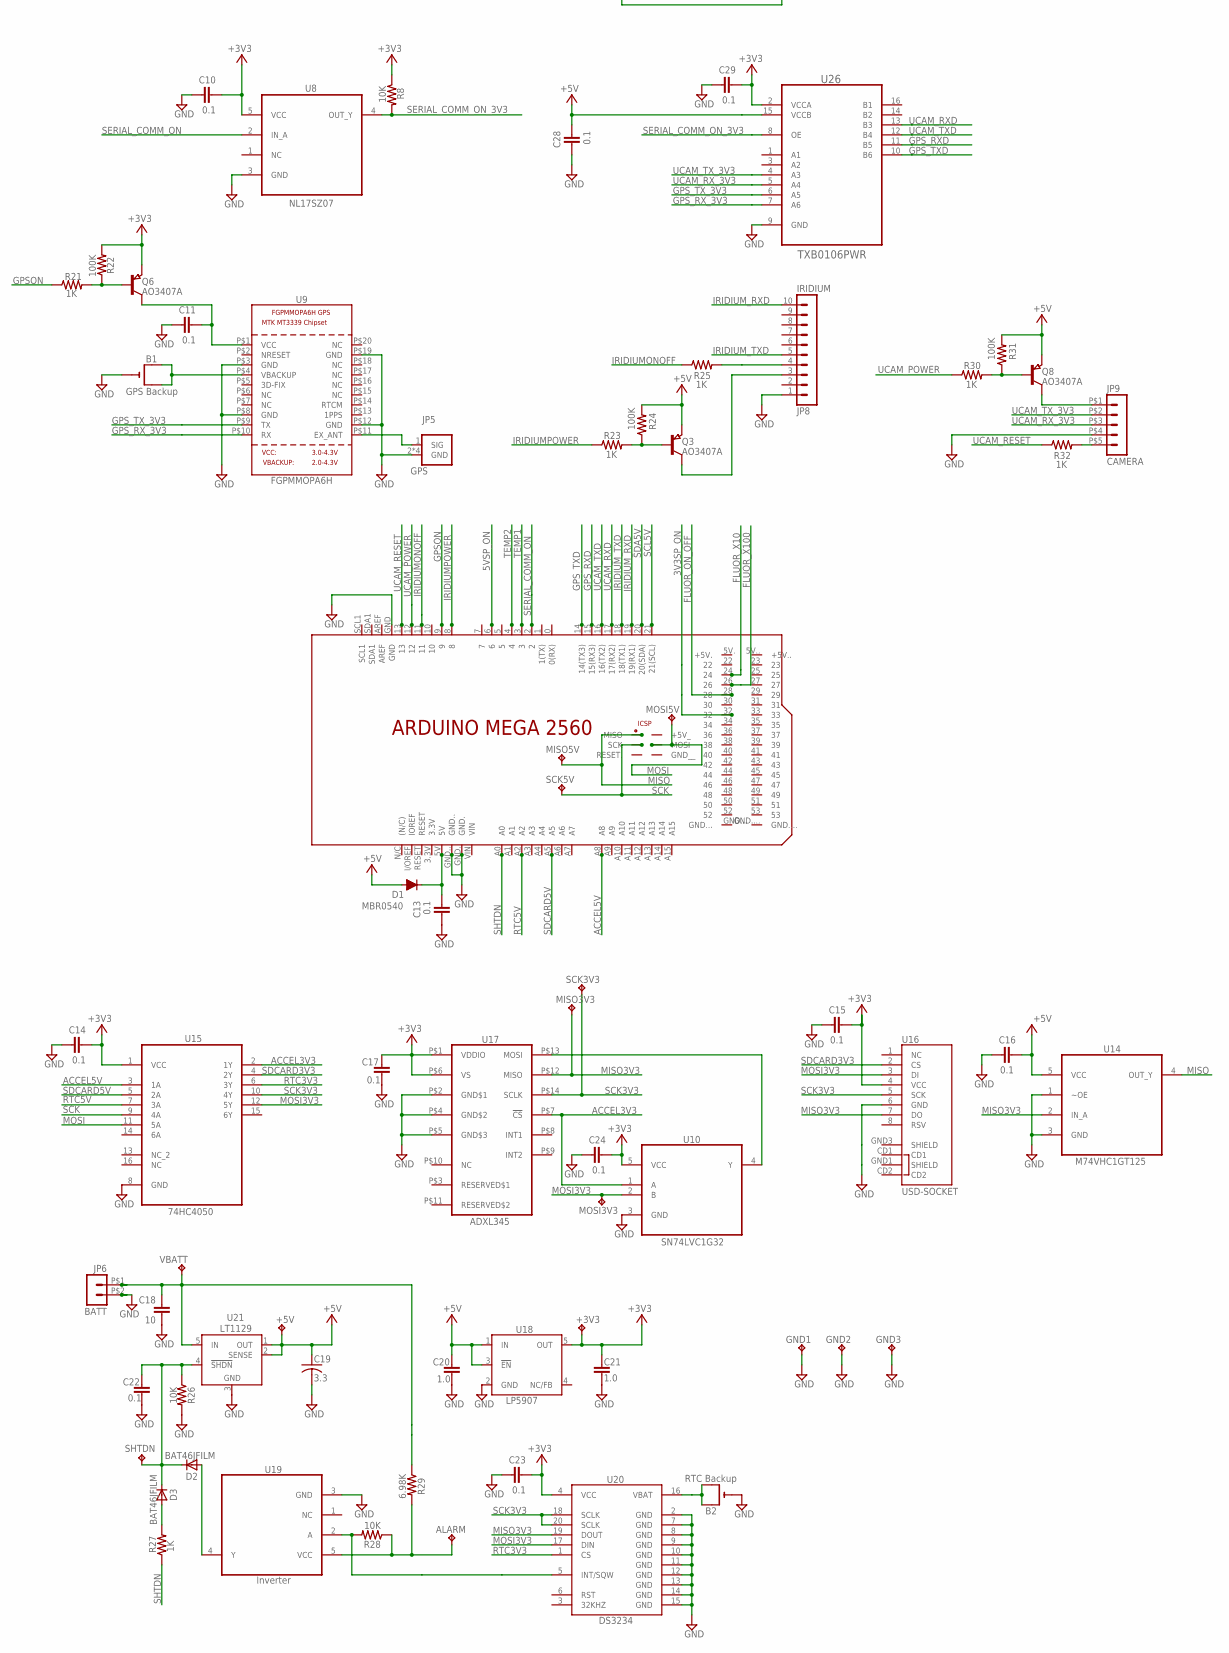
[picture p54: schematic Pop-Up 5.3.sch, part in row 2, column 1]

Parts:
+3V3, +3VP*, +3VT*, +5V: TP-040
ALARM: TP-040
B1: GPS Backup; CR1220-SMD
B2: RTC Backup; CR1220-SMD
C1: 11pF; 0603-CAP; MPN 2222 370 21104
C2, C3, C5, C6, C7, C9, C10, C11, C12, C13, C14, C15, C16, C17, C22, C23, C24, C25, C27, C28, C29: 0.1; 0603-CAP; MPN 2222 370 21104
C4, C8: 4.7; 0603-CAP; MPN 2222 370 21104
C18: 10; C1206
C19: 3.3; C1206
C20, C21: 1.0; 0603-CAP; MPN 2222 370 21104
C26: 10; C1206; MPN 2222 370 21104
D1: MBR0540; SOD123
D2, D3: BAT46JFILM; SOD323-R
GND1, GND2, GND3: TP-040
JP1: PAR; 43650-0215
JP2: PRESSURE; 43650-0415
JP3: SST; 43650-0215
JP4: TEMP; 43650-0215
JP5: GPS; AMPHENOL_901-9895-RFX
JP6: BATT; 43650-0215
JP7: FLUOR; 43045-0612
JP8: IRIDIUM; 53398-1010
JP9: CAMERA; 43650-0515
MISO3V3, MISO5V: TP-040
MOSI3V3, MOSI5V: TP-040
Q1, Q2: BSS138; SOT23
Q3, Q4, Q5, Q6, Q7, Q8: AO3407A; SOT23
R1: 137k,0.1%; R0603
R2: 10k,0.1%; R0603
R3: 2k,0.1%; R0603
R4: 200k; R1206
R5, R7, R9, R11: 3.74K; R0603
R6: 324k; R1206
R8, R10, R26, R28: 10K; R0603
R12: 50k .01%; R2010
R13, R14, R15, R17, R18, R21, R23, R25, R27, R30, R32: 1K; R0603
R16, R19, R20, R22, R24, R31: 100K; R0603
R29: 6.98K; R0603
SCK3V3, SCK5V: TP-040
SCL3V3, SCL5V: TP-040
SDA3V3, SDA5V: TP-040
SHTDN: TP-040
U1, U4: MAX6126; SOIC127P600X175-8N
U2: ADS1100-A1; SOT95P280X145-6N
U3: OPA320; SOT95P280X145-5N
U5, U8: NL17SZ07; SOT65P210X110-5N
U6: ADS1100-A0; SOT95P280X145-6N
U7: ADG836; MSOP10
U9: FGPMMOPA6H
U10: SN74LVC1G32; SOT65P210X110-5N
U11: MAX4624; SOT95P275X100-6N
U12: Arduino MEGA2650; MEGA2650_UPSIDEDOWNMOUNT
U14: M74VHC1GT125; SOT65P210X110-5N
U15: 74HC4050; SOIC127P600X175-16N
U16: USD-SOCKET; MICROSD_1:1
U17: ADXL345; LGA14
U18: LP5907; SOT23-DBV
U19: Inverter; SOT95P280X145-5N
U20: DS3234
U21: LT1129; Q5-DD
U22: LT1013; SOIC127P600X175-8N
U23: LT1634; S8
U24: ADS1100A2; SOT95P280X145-6N
U25: TS5A21366; SOP50P310X90-8N
U26: TXB0106PWR; SOP65P640X120-16N
VBATT: TP-040
VPAR: TP-040

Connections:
3V3SP_ON: R18.1, U12.32
5VSP_ON: R17.1, U12.6
+3V3: +3V3.1, C10.1, C14.1, C15.1, C17.1, C21.1, C23.1, C24.1, C29.1, Q4.2 (E), Q6.2 (E), R8.1, R20.2, R22.2, U8.5 (VCC), U10.5 (VCC), U15.1 (VCC), U16.4 (VCC), U17.P$1 (VDDIO), U17.P$6 (VS), U18.5 (OUT), U20.4 (VCC), U26.2 (VCCA)
+5V: +5V.1, C16.1, C19.1, C20.1, C28.1, D1.2 (A), Q3.2 (E), Q5.2 (E), Q7.2 (E), Q8.2 (E), R16.2, R19.2, R24.2, R31.2, U14.5 (VCC), U18.1 (IN), U18.3 (!EN), U21.1 (OUT), U21.2 (SENSE), U26.15 (VCCB)
ACCEL3V3: U10.1 (A), U15.2 (1Y), U17.P$7 (!CS)
ACCEL5V: U12.A8, U15.3 (1A)
FLUOR_ON_OFF: R15.1, U12.28
FLUOR_X10: R13.1, U12.24
FLUOR_X100: R14.1, U12.26
GND: B1.-, B2.-, C2.2, C3.2, C4.2, C5.1, C6.2, C7.2, C8.2, C9.2, C10.2, C11.2, C12.2, C13.2, C14.2, C15.2, C16.2, C17.2, C18.2, C19.2, C20.2, C21.2, C22.2, C23.2, C24.2, C25.2, C26.2, C27.2, C28.2, C29.2, GND1.1, GND2.1, GND3.1, JP1.P$2 (2), JP2.P$2 (2), JP3.P$1 (1), JP4.P$2 (2), JP5.2 (GND), JP5.3 (GND), JP5.4 (GND), JP5.5 (GND), JP6.P$2 (2), JP7.P$2 (2), JP8.1, JP9.P$4 (4), R3.1, R12.1, R26.2, U1.3 (GND), U1.4 (GNDS), U2.2 (GND), U2.6 (VIN-), U3.2 (V-), U4.3 (GND), U4.4 (GNDS), U5.3 (GND), U6.2 (GND), U6.6 (VIN-), U7.3 (GND), U8.3 (GND), U9.P$3 (GND), U9.P$8 (GND), U9.P$12 (GND), U9.P$19 (GND), U10.3 (GND), U11.3 (GND), U12.GND, U12.GND., U12.GND.., U14.1 (~OE), U14.3 (GND), U15.8 (GND), U16.6 (GND), U17.P$2 (GND$1), U17.P$4 (GND$2), U17.P$5 (GND$3), U18.2 (GND), U19.3 (GND), U20.2 (GND), U20.7 (GND), U20.8 (GND), U20.9 (GND), U20.10 (GND), U20.11 (GND), U20.12 (GND), U20.13 (GND), U20.14 (GND), U20.15 (GND), U21.3 (GND), U22.2 (V-), U24.2 (GND), U25.4 (GND), U26.9 (GND)
GPSON: R21.1, U12.9
GPS_RXD: U12.15 (15(RX3)), U26.11 (B5)
GPS_RX_3V3: U9.P$10 (RX), U26.7 (A6)
GPS_TXD: U12.14 (14(TX3)), U26.10 (B6)
GPS_TX_3V3: U9.P$9 (TX), U26.6 (A5)
IRIDIUMONOFF: R25.1, U12.11
IRIDIUMPOWER: R23.1, U12.8
IRIDIUM_RXD: JP8.10, U12.19 (19(RX1))
IRIDIUM_TXD: JP8.5, U12.18 (18(TX1))
MISO: MISO5V.1, U12.MISO, U14.4 (OUT_Y)
MISO3V3: MISO3V3.1, U14.2 (IN_A), U16.7 (DO), U17.P$12 (MISO), U20.19 (DOUT)
MOSI: MOSI5V.1, U12.MOSI, U15.11 (5A)
MOSI3V3: MOSI3V3.1, U10.2 (B), U15.12 (5Y), U16.3 (DI), U20.17 (DIN)
unnamed: D2.A, U19.4 (Y)
unnamed: Q3.1 (B), R23.2, R24.1
unnamed: ALARM.1, R28.1, R29.2, U19.5 (VCC)
unnamed: JP8.4, R25.2
unnamed: C7.1, U4.1 (NR)
unnamed: C13.1, D1.1 (C), U12.5V
unnamed: U7.2 (S1A), U7.4 (S2A), U11.5 (COM)
unnamed: JP8.3, Q3.3 (C)
unnamed: JP5.1 (SIG), U9.P$11 (EX_ANT)
unnamed: +3VT*.1, C8.1, U4.6 (OUTS), U4.7 (OUTF), U6.5 (VDD)
unnamed: R4.1, R6.2, U23.6 (VOUT)
unnamed: U22.7 (OUTA), U22.8 (-INA), U23.4 (GND)
unnamed: B1.+$1 (+), B1.+$2 (+1), U9.P$4 (VBACKUP)
unnamed: Q6.1 (B), R21.2, R22.1
unnamed: B2.+$1 (+), B2.+$2 (+1), U20.16 (VBAT)
unnamed: R28.2, U19.2 (A), U20.5 (INT/SQW)
unnamed: U6.1 (VIN+), U22.4 (-INB), U22.5 (OUTB)
unnamed: C11.1, Q6.3 (C), U9.P$1 (VCC)
unnamed: JP7.P$3 (3), U24.1 (VIN+)
unnamed: R13.2, U25.7 (IN1)
unnamed: JP7.P$5 (5), U25.2 (COM1)
unnamed: +3VP*.1, C4.1, C5.2, R2.2, U1.6 (OUTS), U1.7 (OUTF), U2.5 (VDD), U3.5 (V+)
unnamed: C3.1, U1.1 (NR)
unnamed: C1.2, R1.2, U2.1 (VIN+), U3.1 (OUT), VPAR.1
unnamed: JP4.P$1 (1), U11.4 (NC)
unnamed: C2.1, R2.1, R3.2, U3.3 (+IN)
unnamed: JP7.P$6 (6), U25.6 (COM2)
unnamed: C1.1, JP1.P$1 (1), R1.1, U3.4 (-IN)
unnamed: C22.1, D2.C, D3.C, R26.1, SHTDN.1, U21.4 (!SHDN)
unnamed: Q5.1 (B), R17.2, R19.1
unnamed: Q4.1 (B), R18.2, R20.1
unnamed: R14.2, U25.3 (IN2)
unnamed: U10.4 (Y), U17.P$13 (MOSI)
unnamed: R6.1, U7.10 (D1), U22.1 (+INA)
unnamed: Q7.1 (B), R15.2, R16.1
unnamed: JP7.P$4 (4), U24.6 (VIN-), U25.1 (NO1), U25.5 (NO2)
unnamed: Q8.1 (B), R30.2, R31.1
unnamed: JP7.P$1 (1), Q7.3 (C)
unnamed: JP9.P$1 (1), Q8.3 (C)
unnamed: C27.1, U7.6 (D2), U22.3 (+INB)
unnamed: JP9.P$5 (5), R32.2
unnamed: D3.A, R27.2
unnamed: JP3.P$2 (2), U11.6 (NO)
unnamed: R10.2, U5.4 (OUT_Y), U7.1 (IN1), U7.5 (IN2)
unnamed: R12.2, U7.7 (S2B), U7.9 (S1B)
RTC3V3: U15.6 (3Y), U20.1 (CS)
RTC5V: U12.A2, U15.7 (3A)
SCK: SCK5V.1, U12.SCK, U15.9 (4A)
SCK3V3: SCK3V3.1, U15.10 (4Y), U16.5 (SCK), U17.P$14 (SCLK), U20.18 (SCLK), U20.20 (SCLK)
SCL3V3: JP2.P$3 (3), Q1.2 (S), R7.1, SCL3V3.1, U2.3 (SCL), U6.3 (SCL)
SCL5V: Q1.3 (D), R9.1, SCL5V.1, U12.21 (21(SCL)), U24.3 (SCL)
SDA3V3: JP2.P$4 (4), Q2.2 (S), R5.1, SDA3V3.1, U2.4 (SDA), U6.4 (SDA)
SDA5V: Q2.3 (D), R11.1, SDA5V.1, U12.20 (20(SDA)), U24.4 (SDA)
SDCARD3V3: U15.4 (2Y), U16.2 (CS)
SDCARD5V: U12.A5, U15.5 (2A)
SERIAL_COMM_ON: U8.2 (IN_A), U12.2
SERIAL_COMM_ON_3V3: R8.2, U8.4 (OUT_Y), U26.8 (OE)
SHTDN: R27.1, U12.A0
TEMP1: U5.2 (IN_A), U12.3
TEMP2: U11.1 (IN), U12.4
UCAM_POWER: R30.1, U12.12
UCAM_RESET: R32.1, U12.13
UCAM_RXD: U12.17 (17(RX2)), U26.13 (B3)
UCAM_RX_3V3: JP9.P$3 (3), U26.5 (A4)
UCAM_TXD: U12.16 (16(TX2)), U26.12 (B4)
UCAM_TX_3V3: JP9.P$2 (2), U26.4 (A3)
VBATT: C18.1, JP6.P$1 (1), R29.1, U21.5 (IN), VBATT.1
VCC/2: C12.1, C25.1, C26.1, Q5.3 (C), R4.2, R9.2, R11.2, U1.2 (IN), U4.2 (IN), U11.2 (V+), U22.6 (V+), U24.5 (VDD), U25.8 (V+)
VDD: C6.1, C9.1, JP2.P$1 (1), Q1.1 (G), Q2.1 (G), Q4.3 (C), R5.2, R7.2, R10.1, U5.5 (VCC), U7.8 (VDD)

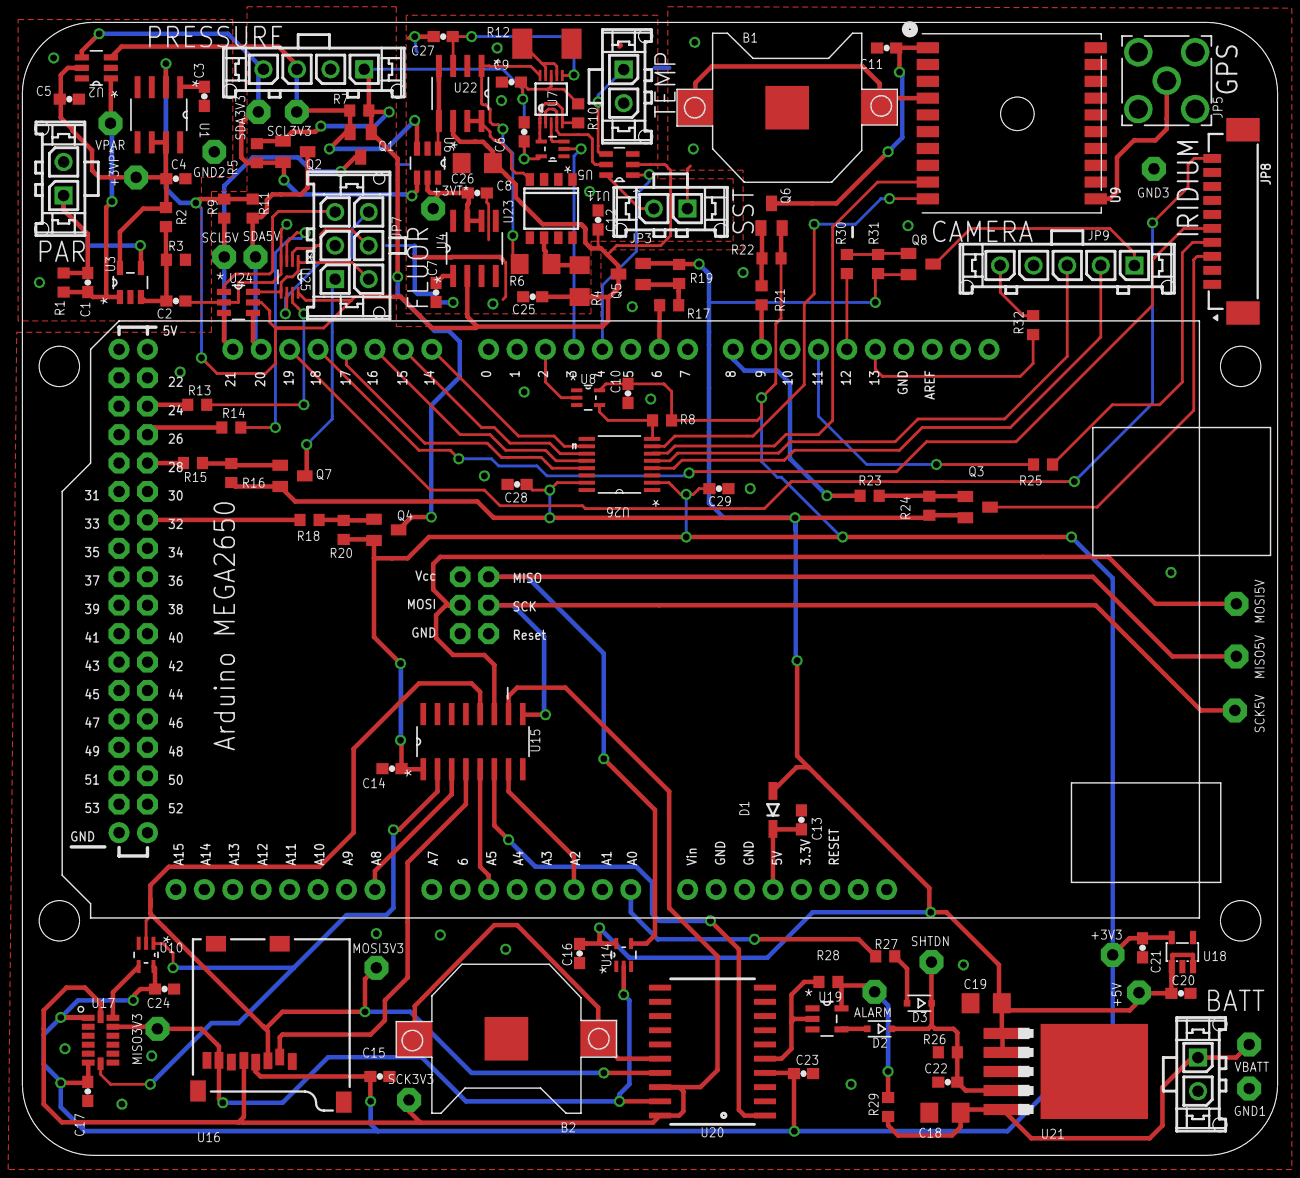
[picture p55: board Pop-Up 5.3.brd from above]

Board: 2 copper layers, 112.1 x 101.2 mm, 129 parts (0 on the bottom side), 92 nets.

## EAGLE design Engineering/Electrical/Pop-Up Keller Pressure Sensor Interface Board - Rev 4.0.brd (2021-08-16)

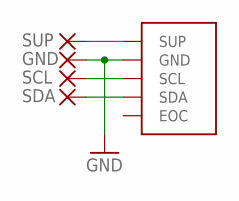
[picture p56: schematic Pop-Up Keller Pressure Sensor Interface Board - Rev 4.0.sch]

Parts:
GND: SMD075X015; SMD-0,75X0,15
P1: 4LD; KELLER-4-LD
SCL: SMD075X015; SMD-0,75X0,15
SDA: SMD075X015; SMD-0,75X0,15
SUP: SMD075X015; SMD-0,75X0,15

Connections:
GND: GND.P$1, P1.GND
unnamed: P1.SUP, SUP.P$1
unnamed: P1.SCL, SCL.P$1
unnamed: P1.SDA, SDA.P$1

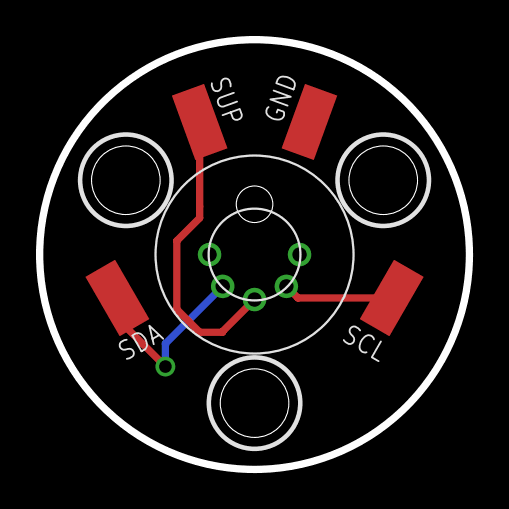
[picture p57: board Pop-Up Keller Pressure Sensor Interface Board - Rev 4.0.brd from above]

Board: 2 copper layers, 23.9 x 23.9 mm, 5 parts (0 on the bottom side), 4 nets.

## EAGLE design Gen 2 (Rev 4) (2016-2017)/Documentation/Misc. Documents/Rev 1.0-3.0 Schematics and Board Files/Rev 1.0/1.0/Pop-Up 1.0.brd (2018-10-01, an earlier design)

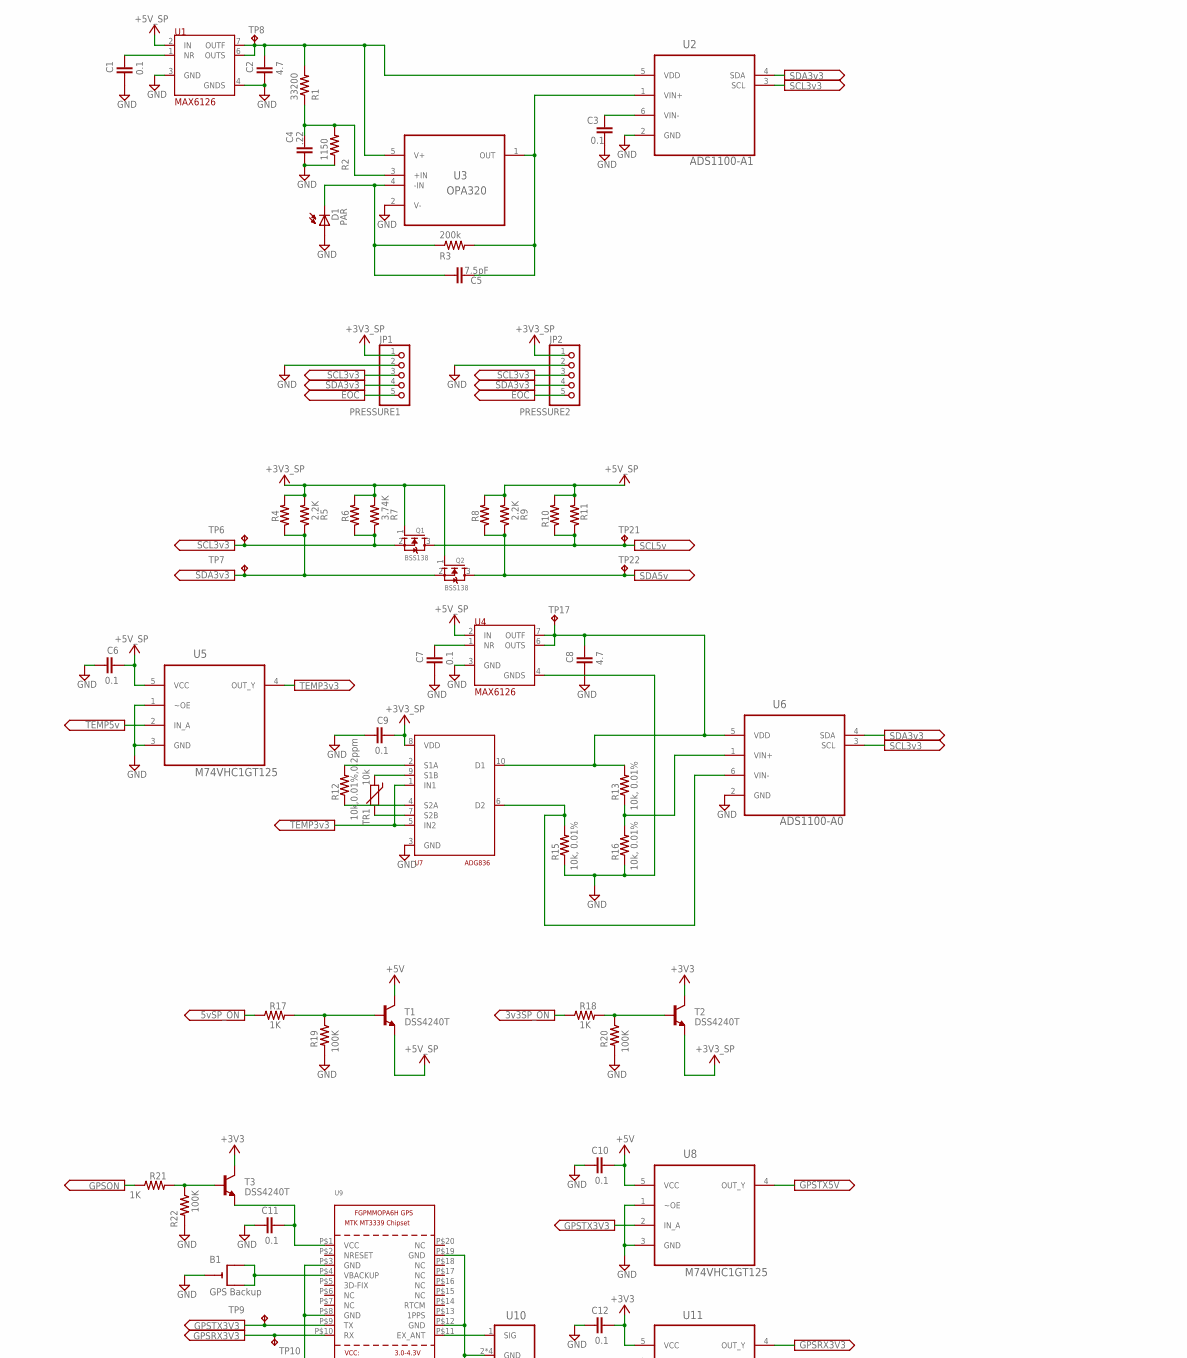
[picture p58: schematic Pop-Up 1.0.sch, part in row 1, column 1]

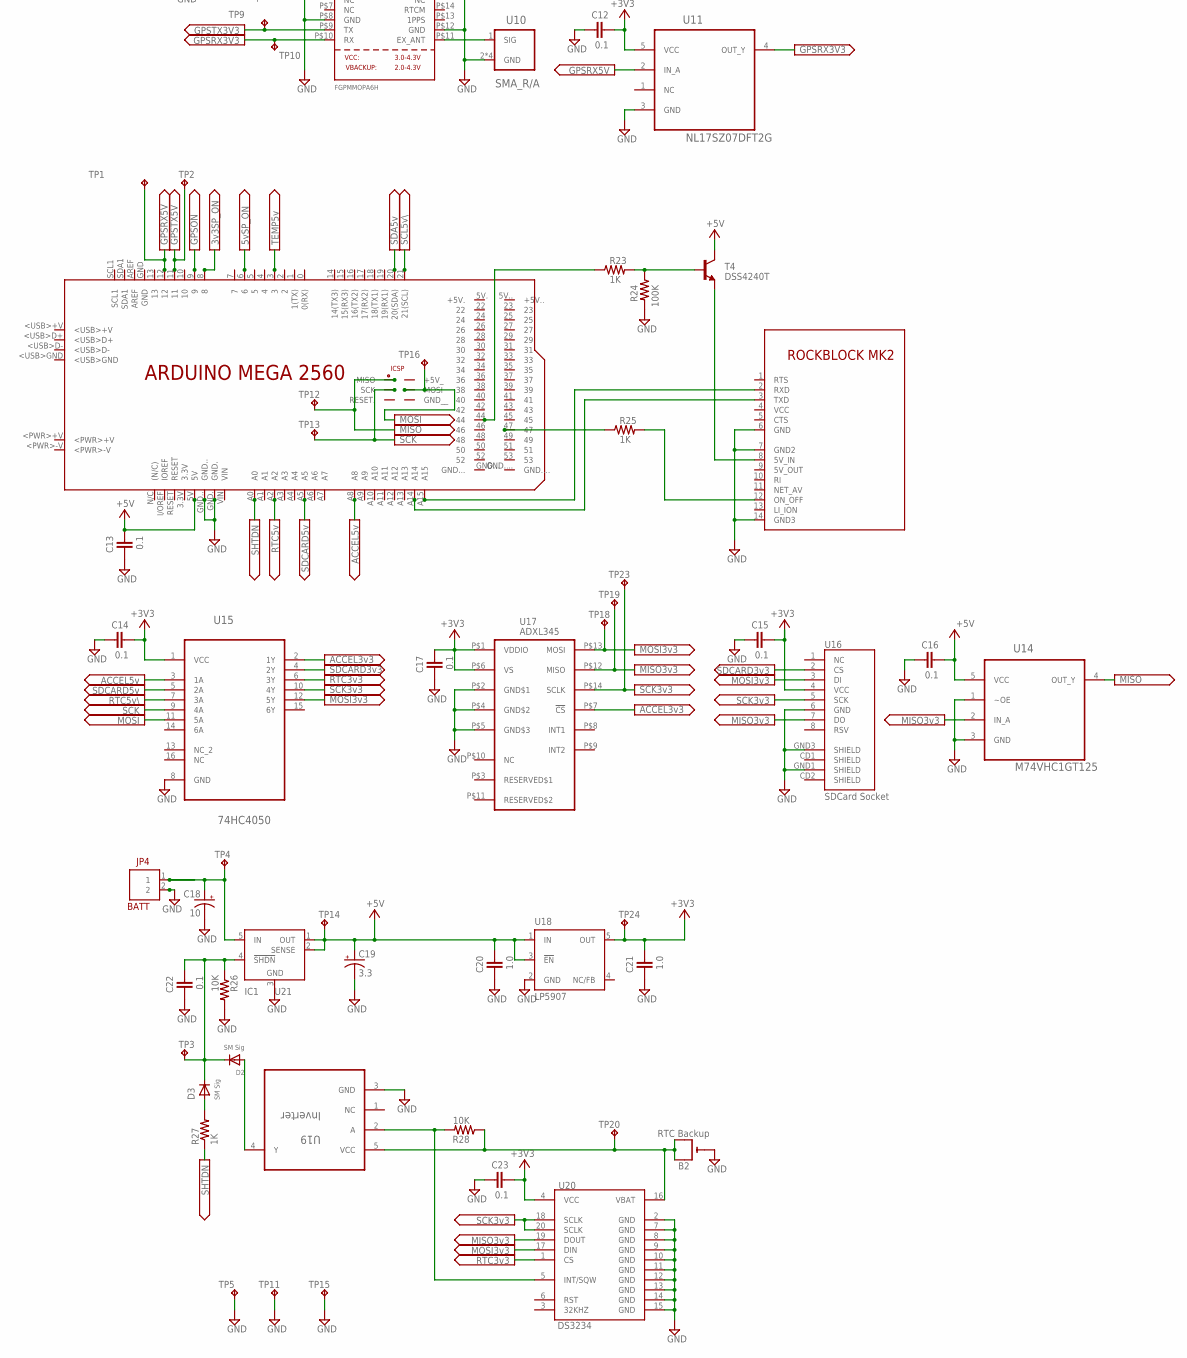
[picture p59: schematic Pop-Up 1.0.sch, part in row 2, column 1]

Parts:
B1: GPS Backup; CR1220-SMD
B2: RTC Backup; CR1220-SMD
C1, C3, C6, C7, C9, C10, C11, C12, C13, C14, C15, C16, C17, C22, C23: 0.1; 0603-CAP; MPN 2222 370 21104
C2, C8: 4.7; 0603-CAP; MPN 2222 370 21104
C4: .22; 0603-CAP; MPN 2222 370 21104
C5: 7.5pF; 0603-CAP; MPN 2222 370 21104
C18: 10; A/3216-18R
C19: 3.3; A/3216-18R
C20, C21: 1.0; 0603-CAP; MPN 2222 370 21104
D1: PAR; SFH225
D2, D3: SM Sig; SOD-323F
IC1: U21; Q5-DD
JP1: PRESSURE1; 1X05
JP2: PRESSURE2; 1X05
JP4: BATT; KK-156-2
Q1, Q2: BSS138; SOT23
R1: 33200; R0603
R2: 1150; R0603
R3: 200k; R0603
R4, R6, R8, R10: R-US_0204/2V; 0204V
R5, R9: 2.2K; R0603
R7: 3.74K; R0603
R11: R-US_R0603; R0603
R12: 10k,0.01%,0.2ppm; R1206
R13, R15, R16: 10k, 0.01%; R0603
R17, R18, R21, R23, R25, R27: 1K; R0603
R19, R20, R22, R24: 100K; R0603
R26, R28: 10K; R0603
T1, T2, T3, T4: DSS4240T; SOT23
TP1, TP2, TP3, TP4, TP5, TP6, TP7, TP8, TP9, TP10, TP11, TP12, TP13, TP14, TP15, TP16, TP17, TP18, TP19, TP20, TP21, TP22, TP23, TP24: TP-063
TR1: 10k; RS-2,5
U1, U4: MAX6126; SOIC127P600X175-8N
U2: ADS1100-A1; SOT95P280X145-6N
U3: OPA320; SOT95P280X145-5N
U5, U8, U14: M74VHC1GT125; SOT65P210X110-5N
U6: ADS1100-A0; SOT95P280X145-6N
U7: ADG836; MSOP10
U9: FGPMMOPA6H
U10: SMA_R/A; AMPHENOL_901-143
U11: NL17SZ07DFT2G; SOT65P210X110-5N
U12: MEGA2650_UPSIDEDOWNMOUNT
U13: ROCKBLOCK_MK2_UPSIDEDOWN
U15: 74HC4050; SOIC127P600X175-16N
U16: SDCard Socket; MICRO-SD-SOCKET-PP
U17: ADXL345; LGA14
U18: LP5907; SOT23-DBV
U19: Inverter; SOT95P280X145-5N
U20: DS3234

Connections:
3V3SP_ON: R18.1, U12.8
5VSP_ON: R17.1, U12.6
+3V3: C12.1, C14.1, C15.1, C17.1, C21.1, C23.1, T2.3 (C), T3.3 (C), TP24.1, U11.5 (VCC), U15.1 (VCC), U16.4 (VCC), U17.P$1 (VDDIO), U17.P$6 (VS), U18.5 (OUT), U20.4 (VCC)
+3V3SP: C9.1, JP1.1, JP2.1, Q1.1 (G), Q2.1 (G), R4.2, R5.2, R6.2, R7.2, T2.2 (E), U7.8 (VDD)
+5V: C10.1, C13.1, C16.1, C19.+, C20.1, IC1.1 (OUT), IC1.2 (SENSE), T1.3 (C), T4.3 (C), TP14.1, U8.5 (VCC), U12.5V, U14.5 (VCC), U18.1 (IN), U18.3 (!EN)
+5V_SP: C6.1, R8.2, R9.2, R10.2, R11.2, T1.2 (E), U1.2 (IN), U4.2 (IN), U5.5 (VCC)
ACCEL3V3: U15.2 (1Y), U17.P$7 (!CS)
ACCEL5V: U12.A8, U15.3 (1A)
EOC1: JP1.5
EOC2: JP2.5
GND: B1.-, B2.-, C1.2, C2.2, C3.1, C4.2, C6.2, C7.2, C8.2, C9.2, C10.2, C11.2, C12.2, C13.2, C14.2, C15.2, C16.2, C17.2, C18.-, C19.-, C20.2, C21.2, C22.2, C23.2, D1.A, IC1.3 (GND), JP1.2, JP2.2, JP4.2, R2.1, R15.1, R16.1, R19.2, R20.2, R22.2, R24.2, R26.2, TP5.1, TP11.1, TP15.1, U1.3 (GND), U1.4 (GNDS), U2.2 (GND), U3.2 (V-), U4.3 (GND), U4.4 (GNDS), U5.1 (~OE), U5.3 (GND), U6.2 (GND), U7.3 (GND), U8.1 (~OE), U8.3 (GND), U9.P$3 (GND), U9.P$8 (GND), U9.P$12 (GND), U9.P$19 (GND), U10.2 (GND), U10.3 (GND), U10.4 (GND), U10.5 (GND), U11.3 (GND), U12.GND., U12.GND.., U13.6 (GND), U13.7 (GND2), U13.14 (GND3), U14.1 (~OE), U14.3 (GND), U15.8 (GND), U16.6 (GND), U16.GND1 (SHIELD), U16.GND3 (SHIELD), U17.P$2 (GND$1), U17.P$4 (GND$2), U17.P$5 (GND$3), U18.2 (GND), U19.3 (GND), U20.2 (GND), U20.7 (GND), U20.8 (GND), U20.9 (GND), U20.10 (GND), U20.11 (GND), U20.12 (GND), U20.13 (GND), U20.14 (GND), U20.15 (GND)
GPSON: R21.1, U12.9
GPSRX3V3: TP10.1, U9.P$10 (RX), U11.4 (OUT_Y)
GPSRX5V: TP1.1, U11.2 (IN_A), U12.12
GPSTX3V3: TP9.1, U8.2 (IN_A), U9.P$9 (TX)
GPSTX5V: TP2.1, U8.4 (OUT_Y), U12.11
MISO: TP12.1, U12.MISO, U14.4 (OUT_Y)
MISO3V3: TP19.1, U14.2 (IN_A), U16.7 (DO), U17.P$12 (MISO), U20.19 (DOUT)
MOSI: TP16.1, U12.MOSI, U15.11 (5A)
MOSI3V3: TP18.1, U15.12 (5Y), U16.3 (DI), U17.P$13 (MOSI), U20.17 (DIN)
unnamed: D2.A, U19.4 (Y)
unnamed: R23.2, R24.1, T4.1 (B)
unnamed: B2.+$1 (+), B2.+$2 (+1), R28.1, TP20.1, U19.5 (VCC), U20.16 (VBAT)
unnamed: R25.2, U13.12 (ON_OFF)
unnamed: C7.1, U4.1 (NR)
unnamed: R25.1, U12.47
unnamed: TR1.1, U7.9 (S1B)
unnamed: R23.1, U12.44
unnamed: T4.2 (E), U13.8 (5V_IN)
unnamed: U9.P$11 (EX_ANT), U10.1 (SIG)
unnamed: C8.1, R13.2, TP17.1, U4.6 (OUTS), U4.7 (OUTF), U6.5 (VDD), U7.10 (D1)
unnamed: R15.2, U6.6 (VIN-), U7.6 (D2)
unnamed: TR1.2, U7.7 (S2B)
unnamed: B1.+$1 (+), B1.+$2 (+1), U9.P$4 (VBACKUP)
unnamed: R21.2, R22.1, T3.1 (B)
unnamed: R13.1, R16.2, U6.1 (VIN+)
unnamed: R28.2, U19.2 (A), U20.5 (INT/SQW)
unnamed: U12.A14, U13.3 (TXD)
unnamed: C11.1, T3.2 (E), U9.P$1 (VCC)
unnamed: U12.A15, U13.2 (RXD)
unnamed: R12.1, U7.4 (S2A)
unnamed: R12.2, U7.2 (S1A)
unnamed: C2.1, R1.2, TP8.1, U1.6 (OUTS), U1.7 (OUTF), U2.5 (VDD), U3.5 (V+)
unnamed: C1.1, U1.1 (NR)
unnamed: C5.2, R3.2, U2.1 (VIN+), U3.1 (OUT)
unnamed: C3.2, U2.6 (VIN-)
unnamed: C4.1, R1.1, R2.2, U3.3 (+IN)
unnamed: C5.1, D1.K (C), R3.1, U3.4 (-IN)
unnamed: C22.1, D2.C, D3.C, IC1.4 (!SHDN), R26.1, TP3.1
unnamed: R17.2, R19.1, T1.1 (B)
unnamed: R18.2, R20.1, T2.1 (B)
unnamed: D3.A, R27.2
RTC3V3: U15.6 (3Y), U20.1 (CS)
RTC5V: U12.A2, U15.7 (3A)
SCK: TP13.1, U12.SCK, U15.9 (4A)
SCK3V3: TP23.1, U15.10 (4Y), U16.5 (SCK), U17.P$14 (SCLK), U20.18 (SCLK), U20.20 (SCLK)
SCL3V3: JP1.3, JP2.3, Q1.2 (S), R6.1, R7.1, TP6.1, U2.3 (SCL), U6.3 (SCL)
SCL5V: Q1.3 (D), R10.1, R11.1, TP21.1, U12.21 (21(SCL))
SDA3V3: JP1.4, JP2.4, Q2.2 (S), R4.1, R5.1, TP7.1, U2.4 (SDA), U6.4 (SDA)
SDA5V: Q2.3 (D), R8.1, R9.1, TP22.1, U12.20 (20(SDA))
SDCARD3V3: U15.4 (2Y), U16.2 (CS)
SDCARD5V: U12.A5, U15.5 (2A)
SHTDN: R27.1, U12.A0
TEMP3V3: U5.4 (OUT_Y), U7.1 (IN1), U7.5 (IN2)
TEMP5V: U5.2 (IN_A), U12.3
VBATT: C18.+, IC1.5 (IN), JP4.1, TP4.1

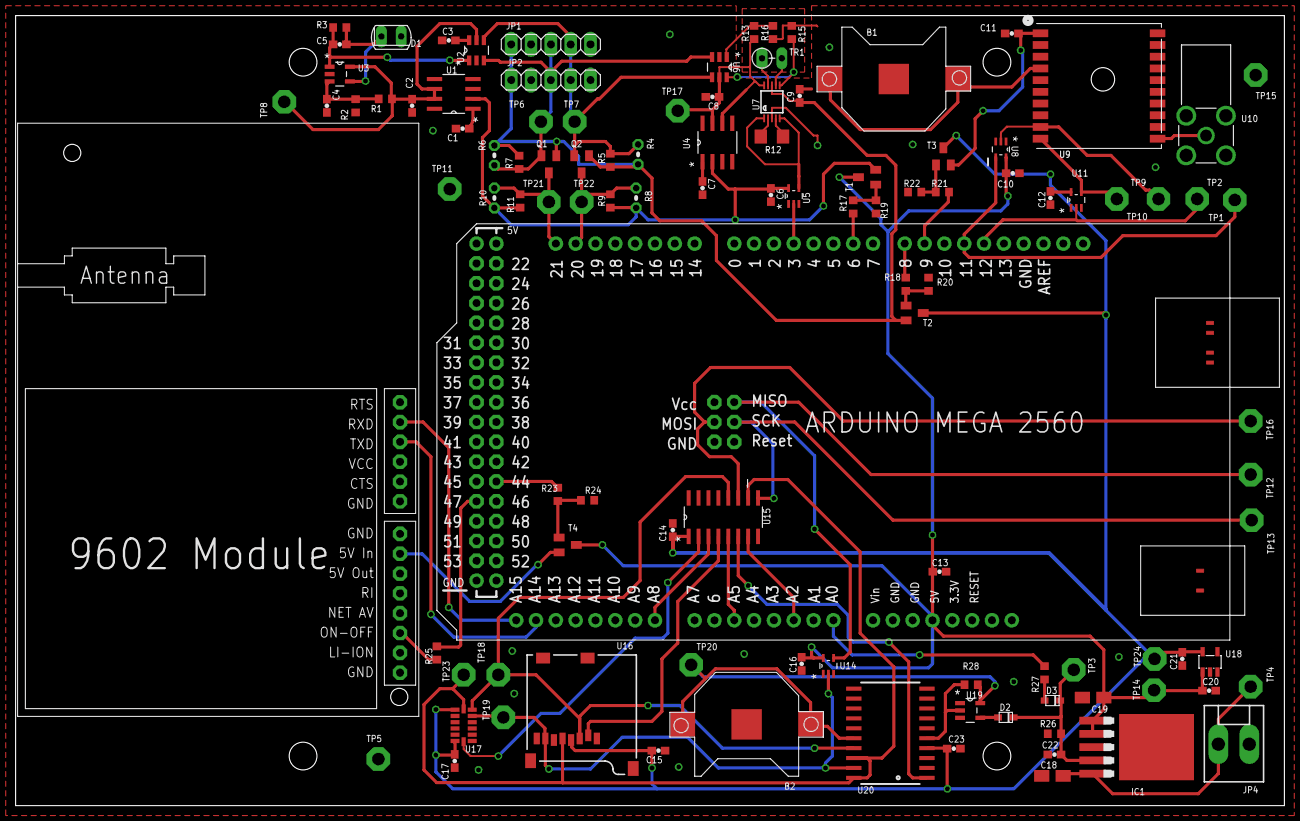
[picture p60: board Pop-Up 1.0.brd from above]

Board: 2 copper layers, 162.6 x 101.2 mm, 110 parts (0 on the bottom side), 64 nets.

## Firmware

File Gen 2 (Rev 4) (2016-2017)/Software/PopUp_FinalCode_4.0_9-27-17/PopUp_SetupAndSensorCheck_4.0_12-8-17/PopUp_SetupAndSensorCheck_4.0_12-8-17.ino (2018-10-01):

//include various libraries
#include <ctype.h>
#include <math.h>                      //Library for math functions used in calculating sensor values
#include <Wire.h>                      //Library for I2C Comms
#include <SPI.h>                       //Library for SPI Comms
#include <SD.h>                        //Library for SD Card
#include <RTClib.h>                    //Library for RTC Functions
#include <RTC_DS3234.h>                //Library for Ds3234 RTC
#include <SoftwareSerial.h>            //Library to read/write serial data on I/O pins (for GPS)
#include <MemoryFree.h>                //Library to determine amount of free RAM while program is running
#include <TinyGPS++.h>                 //Library for interfacing with GPS module
#include <IridiumSBD.h>                //Library for Iridium interface - rockBlock Mk2

#define TEMP_SWITCH 3                  //Define pin for switching between temp sensor and reference thermistor
#define SENSOR_POWER_5V 6              //Define pin for switching on power to 5V sensors
#define SENSOR_POWER_3V3 22            //Define pin for switching on power to 3.3V sensors
#define GPS_POWER 9                    //Define pin for switching on GPS
#define IRIDIUM_POWER 8                //Define pin for switching on Iridium power
#define IRIDIUM_ON_OFF A6              //Define pin for switching on Iridium module
#define ACCEL_CS A8                    //Define pin for accelerometer SPI chip select
#define SDCARD_CS A5                   //Define pin for sdcard SPI chip select
#define RTC_CS A2                      //Define pin for RTC SPI chip select
#define SHUTDOWN A0                    //Define pin for shutting down unit
#define GPS_TX 11                      //Define pin for GPS Serial TX data
#define GPS_RX 12                      //Define pin for GPS Serial RX data

#define keller3bar 0x40       		//Define pressure sensor control register
#define keller10bar 0x41      		//Define pressure sensor control register
#define checkpressure 0xAC    		//Define pressure sensor control register
#define ads1100A0 0x48        		//Define tempADC control register
#define ads1100A1 0x49        		//Define parADC control register
#define RECEIVE_BUFFER_SIZE 15		//Size of buffer to receive Iridium Messages
#define FAILSAFE_TIMER 86400            //Alarm for Failsafe if program freezes somehow 		(nominal FAILSAFE_TIMER 86400 = 1 day)
#define CHARS_PER_SBDMESSAGE 100        //Number of bytes to pull from data file and send at once	(nominal CHARS_PER_SBDMESSAGE 100 = 100 bytes)
#define GPS_SEARCH_SECONDS 120		//Number of seconds to search for GPS signal		        (nominal GPS_SEARCH_SECONDS 120	= 2 minutes)
#define GPS_SECONDS_BETWEEN_SEARCHES 20	//Number of seconds between GPS Searches to send data	        (nominal GPS_SECONDS_BETWEEN_SEARCHES 180 = 3 minutes)
#define GPS_SUCCESSES_TO_SEND 1		//Number of successful gps hits before sending data	        (nominal GPS_SUCCESSES_TO_SEND 3 = 3 attempts)
#define SEND_DATA_INTERVAL 300		//Default interval to send data once GPS has been found	        (nominal SEND_DATA_INTERVAL 300 = 5 minutes)

SoftwareSerial ss(GPS_TX,GPS_RX);		//Software Serial Object for GPS Communication 
IridiumSBD isbd(Serial1,IRIDIUM_ON_OFF);	//ISBD Object for Iridium Commands
TinyGPSPlus gps;			        //Object for GPS commands and data
RTC_DS3234 RTC(RTC_CS);			        //Object for RTC

DateTime wakeupTime;				//Global Variable for when unit first wakes
DateTime alarmtime;			        //Global Variable for RTC Alarm
boolean foundGPS=false; 			//Global Variable for GPS lock success
char whichFile='s';			        //Global variable to designate which file to read when sending data.  's' = summary (first message to send)
unsigned long filePosition=0;			//Global variable to designate position in file when sending data
boolean newFile=true;                           
boolean beginSDsuccess;
//********************************************************************************************************************************************************//
//***SET DATES AND PROGRAM INTERVALS HERE*****************************************************************************************************************//
//********************************************************************************************************************************************************//

DateTime unitStart =  DateTime(17,3,1,11,0,0);             //Date and Time for first sample: 				DateTime(YEAR,MON,DAY,HOUR,MIN,SEC);
DateTime releaseTime =  DateTime(17,4,1,15,0,0);            //Date and Time for actual release of burn wire: 		DateTime(YEAR,MON,DAY,HOUR,MIN,SEC);
DateTime sendDataDate = DateTime(17,4,1,18,0,0);            //Date and Time to attempt data transmission twice a day: 	DateTime(YEAR,MON,DAY,HOUR,MIN,SEC);
DateTime iceFreeDate = DateTime(17,4,1,20,0,0);             //Date and Time to attempt data transmission every hour: 	DateTime(YEAR,MON,DAY,HOUR,MIN,SEC);
#define FAILSAFE_TIMER 86400				    //Alarm for Failsafe if program freezes somehow 		(nominal FAILSAFE_TIMER 86400 = 1 day)
#define BOTTOM_SAMPLE_INTERVAL 300			    //Interval between bottom samples 				(nominal BOTTOM_SAMPLE_INTERVAL 21600 = 6 hours)
#define PRE_RELEASE_WAKEUP_TIME 3600			    //How long before planned release to wait for profile 	(nominal PRE_RELEASE_WAKEUP_TIME 21600 = 6 hours)
#define UNDER_ICE_SAMPLE_INTERVAL 7200			    //Interval between samples at the surface (or uncer ice)	(nominal UNDER_ICE_SAMPLE_INTERVAL 3600	= 1 hour)
#define PROFILE_LENGTH_SECONDS 60			    //Length of profile in seconds				(nominal PROFILE_LENGTH_SECONDS 60 = 60 seconds)
#define DEPTH_CHANGE_TO_TRIP_PROFILE 2			    //Depth in meters needed to begin profile mode		(nominal DEPTH_CHANGE_TO_TRIP_PROFILE 3	= 3 meters)
#define GPS_SEARCH_SECONDS 90				    //Number of seconds to search for GPS signal		(nominal GPS_SEARCH_SECONDS 120	= 2 minutes)
#define GPS_SECONDS_BETWEEN_SEARCHES 20		            //Number of seconds between GPS Searches to send data	(nominal GPS_SECONDS_BETWEEN_SEARCHES 180 = 3 minutes)
#define GPS_SUCCESSES_TO_SEND 1				    //Number of successful gps hits before sending data		(nominal GPS_SUCCESSES_TO_SEND 3 = 2 attempts)
#define CHARS_PER_SBDMESSAGE 100		            //Number of bytes to pull from data file and send at once	(nominal CHARS_PER_SBDMESSAGE 50 = 50 bytes)
#define RECEIVE_BUFFER_SIZE 15		                    //Number of bytes to pull from data file and send at once	(nominal CHARS_PER_SBDMESSAGE 50 = 50 bytes)
#define SEND_DATA_INTERVAL 300		                    //Default interval to send data once GPS has been found	(nominal SEND_DATA_INTERVAL 1800 = 30 minutes)

//********************************************************************************************************************************************************//
//***END PROGRAM DATES AND SAMPLE INTERVAL SECTION********************************************************************************************************//
//********************************************************************************************************************************************************//

void setup(){
    initializePins();		                //Initialize Arduino Pins for Output and Set Voltage Levels
    Wire.begin();				//Start I2C Communication
    SPI.begin();                                //Start up SPI Communication (needed for various ICs) 
    SPI.setDataMode(SPI_MODE2);                 //Set SPI Data Mode
    SPI.setBitOrder(MSBFIRST);                  //Configure SPI Communication (needed for various ICs)
    SPI.setClockDivider(SPI_CLOCK_DIV16);       //Set SPI Clock Speed

    setupRTCandSD();			        //Start RTC and SD Card 
    setupAccel();		                //Start Accelerometer

    turnOn3v3SensorPower();		        //turn on 3.3V Power to sensors (PAR, TEMP, PRESSURE)
    turnOn5vSensorPower();		        //turn on 5V Power to sensors (Needed for 5V I2C communication)
    delay(50);				        //Short delay here to start ADCs
    setupTempADC();			        //Start Up the ADC for Temperature Measurement
    setupPARADC();			        //Start Up the ADC for PAR Measurement
    delay(500);				        //Longer delay here to let voltages stabilize
  
    Serial.begin(115200);                       //Turn the Serial Protocol ON
    Serial.println(F("Set up Complete!!"));
    displayStatus();
    delay(2000); 
}

void loop(){
      //"OPTIONS" Menu
      Serial.println(F("-----------------------------------------------"));
      Serial.println(F("'1' - display Status"));
      Serial.println(F("'2' - set RTC time/date"));
      Serial.println(F("'3' - display SD Card Data"));
      Serial.println(F("'4' - check Temperature Sensor"));
      Serial.println(F("'5' - check Pressure Sensors"));
      Serial.println(F("'6' - check Accelerometer (Tilt Sensor)"));
      Serial.println(F("'7' - check PAR"));
      Serial.println(F("'8' - check GPS"));
      Serial.println(F("'9' - check Iridium"));
      Serial.println(F("'P' - collect PAR calibration data"));
      Serial.println(F("'X' - delete all SD Card Data"));
      Serial.println(F("-----------------------------------------------"));
      Serial.println();
      
      DateTime now = RTC.now();
      byte byteRead;   //variable to read Serial input from user
      boolean waiting=true;  //variable to wait for user input

      while(waiting==true){        //Run loop to set unit status as long as serial connection exists
        byteRead = Serial.read();   //read serial input (keystroke from user)
        switch (byteRead){   
          case  49 : //if user enters '1', display unit Status
            displayStatus();
            waiting=false;
            break;
          case  50 : //if user enters '2', display dialog to have user set RTC
            setRTC();
            waiting=false;
            break;
          case  51 : //if user enters '3', check SD Card Data
            sdDataCheck();
            waiting=false;
            break;
          case  52 : //if user enters '4', check Temperature
            //break intentionally omitted, go to displaySensor() function
          case  53 : //if user enters '5', check Pressure
            //break intentionally omitted, go to displaySensor() function
          case  54 : //if user enters '6', check Accelerometer
            //break intentionally omitted, go to displaySensor() function
          case  55 : //if user enters '7', check PAR
            displaySensor(byteRead);
            waiting=false;
            break;
          case  56 : //if user enters '8', check GPS
            checkGPS();
            waiting=false;
            break;
          case  57 : //if user enters '9', check Iridium
            checkIridium();
            waiting=false;
            break;
          case  80 : //if user enters 'P', enter PAR calibration mode
            calibratePAR();
            waiting=false;
            break;
          case  88 : //if user enters 'X', delete files from SD Card
            deleteFiles();
            waiting=false;
            break;
        }
      }
      delay(2000);   //wait a few seconds before running the loop again
}
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

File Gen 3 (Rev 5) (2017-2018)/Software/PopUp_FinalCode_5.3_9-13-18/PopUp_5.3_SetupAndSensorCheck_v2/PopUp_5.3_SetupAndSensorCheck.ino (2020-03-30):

//INPUT for POP-UP S/N
#define SN 2018                       //INPUT POP-UP S/N as SN = ####

//INPUT for Topside Temperature Probe (TTP)
float At = 0.00117611211;  //INPUT Steinhart-Hart Coeficient A for probes from unit of interest
float Bt = 0.000231799033;  //INPUT Steinhart-Hart Coeficient B for probes from unit of interest
float Ct = 0.000000106066762;  //INPUT Steinhart-Hart Coeficient C for probes from unit of interest

//INPUT for Sea Surface Temperature (SST) Probe
float As = 0.00105471332;  //INPUT Steinhart-Hart Coeficient A for probes from unit of interest
float Bs = 0.00024840849;   //INPUT Steinhart-Hart Coeficient B for probes from unit of interest
float Cs = 0.0000000603057951;  //INPUT Steinhart-Hart Coeficient C for probes from unit of interest


//include various libraries
#include <ctype.h>
#include <math.h>                      //Library for math functions used in calculating sensor values
#include <Wire.h>                      //Library for I2C Comms
#include <SPI.h>                       //Library for SPI Comms
#include <SD.h>                        //Library for SD Card
#include <RTClib.h>                    //Library for RTC Functions
#include <RTC_DS3234.h>                //Library for DS3234 RTC
#include <MemoryFree.h>                //Library to determine amount of free RAM while program is running
#include <TinyGPS++.h>                 //Library for interfacing with GPS module
#include <IridiumSBD.h>                //Library for Iridium interface - rockBlock Mk3

#define TEMP_SWITCH_1 3                //Define pin for switching between temp sensors and reference thermistors
#define TEMP_SWITCH_2 4                //Define pin for switching between temp sensors and reference thermistors
#define SENSOR_POWER_5V 6              //Define pin for switching on power to 5V sensors
#define SENSOR_POWER_3V3 32            //Define pin for switching on power to 3.3V sensors
#define GPS_POWER 9                    //Define pin for switching on GPS
#define IRIDIUM_POWER 8                //Define pin for switching on Iridium power
#define IRIDIUM_ON_OFF 11              //Define pin for switching on Iridium module
#define ACCEL_CS A8                    //Define pin for accelerometer SPI chip select
#define SDCARD_CS A5                   //Define pin for sdcard SPI chip select
#define RTC_CS A2                      //Define pin for RTC SPI chip select
#define SHUTDOWN A0                    //Define pin for shutting down unit
#define FLUOROMETER_X10 24             //Define pin for setting Fluorometer Sensitivity to X10
#define FLUOROMETER_X100 26            //Define pin for setting Fluorometer Sensitivity to X100
#define FLUOROMETER_ON_OFF 28          //Define pin for switching on Fluorometer
#define CAMERA_RESET 13                //Define pin for switching on Camera reset function
#define CAMERA_ON_OFF 12               //Define pin for switching on Camera module
#define SERIAL_COMMS_ON_OFF 2          //Define pin for switching on Serial Comms chip (5V to 3.3V translator)
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

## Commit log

2018-12-13 Rename prototype201_test1_07Dec18_deploymentdialog.txt to testing winter 2018-2019/prototype201_test1_07Dec18_deploymentdialog.txt
2018-12-13 Rename testing winter 2018-2019/prototype201_test1_07Dec18_deploymentdialog.txt to testing winter 2018-2019/deployment dialogs/prototype201_test1_07Dec18_deploymentdialog.txt
2019-03-05 Initial Commit.
    File is reformatted to include all surface data from Pop Ups 003, 004, 005 & 006 deployed in Fall of 2017 and data recovered in Spring of 2018.
    [FY17_ALL_SURFACE_DATA.xlsx]
2019-07-05 Add data and jupyter analysis scripts
    [201_TB119148_BOTDAT.csv, 300434063823800_bottom_data.csv, 300434063823800_ice_data.csv, 300434063823800_profile_data.csv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]
2019-07-05 update July 5 2019
    - 300434063823800
    - 300434063921240
    [300434063823800_sst_data.csv, 300434063921240_sst_data.csv, message_position_2019.csv]
2019-07-08 July 8 2019 Data Update
    [300434063823800_sst_data.csv, 300434063921240_sst_data.csv, message_position_2019.csv]
2019-07-08 July 8 2019 Data update 2
    [300434063823800_sst_data.csv]
2019-07-09 July 9 2019 Update and new ID
    # 2018 - 300434063823800 - C10/C11 Popup 102 : Active
    # 2018 - 300434063921240 - C2 Popup 101 : Active
    # 2018 - 300434063928220 - Popup 103 : Active **NEW**
    [300434063823800_sst_data.csv, 300434063921240_bottom_data.csv, 300434063921240_ice_data.csv, 300434063921240_profile_data.csv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]
2019-07-09 July 9 2019 Update 2
    reprocessing of clocks
    [300434063823800_bottom_data.csv, 300434063823800_ice_data.csv, 300434063823800_sst_data.csv, 300434063921240_bottom_data.csv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]
2019-07-11 July 10 2019 Update
    [300434063921240_bottom_data.csv, 300434063921240_ice_data.csv, 300434063921240_profile_data.csv, 300434063921240_sst_data.csv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]
2019-07-16 July 16 2019 Update
    [300434063823800_sst_data.csv, 300434063921240_sst_data.csv, 300434063928220_sst_data.csv, message_position_2019.csv]
2019-07-17 update imei location output for erddap usage
    [message_position_2019.csv]
2019-07-31 July 31 2019 Update
    [300434063823800_sst_data.csv, 300434063921240_sst_data.csv, 300434063928220_sst_data.csv, message_position_2019.csv]
2019-08-02 Aug 2 2019 Popup update
    [300434063823800_sst_data.csv, 300434063921240_sst_data.csv, message_position_2019.csv]
2019-08-15 Aug 15 2019 Update
    [300434063823800_sst_data.csv, 300434063921240_sst_data.csv, message_position_2019.csv]
2019-10-26 remove data from archive and place in ecoraid
    [300434063823800_bottom_data.csv, 300434063823800_ice_data.csv, 300434063823800_profile_data.csv, 300434063823800_sst_data.csv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]
2020-03-27 Function to Arduino Setup Code
    Temperature Response Test Function added to Arduino Setup Code, now SetupAndSensorCheck_v2
2020-03-30 setup sensor check notes edit
    small edits to comments and instructions in the code
2021-08-16 Archive original repo, add working folders
    moved prior file organization into archive. Current file organization has data processing files under "Data". All data processing scripts in Jupyter notebook have relative paths and use os.path.join 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
    [0200_bottom_data.csv, 0200_ice_data.csv, 0200_profile_data.csv, 0200_sst_data.csv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]
2021-08-16 Add in Data folder, error committing last time
    Data folder was previously saved as repo on private account, integrated into EcoFOCI_PopUp repo and deleted private repo .git
    [18_02_300434063823800_bottom_data.csv, 18_02_300434063823800_ice_data.csv, 18_02_300434063823800_profile_data.csv, 18_02_300434063823800_sst_data.csv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]
2021-08-17 remove gitignore
    remove gitignore so that photos from camera output in Data are included in repo
    [201_TB119148_BOTDAT.csv, 9200_bottom_data.csv, 9200_ice_data.csv, message_position_.csv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]
2021-08-19 Add Background and Instruction Jupyter Notebooks
    Cleaned up a few files, added instruction files
    [18_02_300434063823800_bottom_data.csv, 18_02_300434063823800_ice_data.csv, 18_02_300434063823800_profile_data.csv, 18_02_300434063823800_sst_data.csv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]
2021-08-24 add .yaml files
    add .yaml files to data>yaml , re-run temp cal coeff.
    [300434063924230_bottom_data.csv, 300434063924230_ice_data.csv, 300434063924230_profile_data.csv, 300434063924230_sst_data.csv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]
2021-08-25 temperature conversion log10 added back
    version == 1 added log10 back to Translator script
    [message_position.csv]
2021-08-30 Untrack Data
    untrack raw data (sbd messages are available internally)
    untrack output results data (this shouldn't be freely available here) - work with S.Bell to make data available via ERDDAP
    [300434063470010_bottom_data.csv, 300434063477010_bottom_data.csv, 300434063823800_bottom_data.csv, 300434063823800_ice_data.csv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]
2022-02-14 Create 03_PopUpFloat_Translater_19bs8apoptop.ipynb
    - this unit used the temperature calculation - version=1 and is unique enough to have its own record
2022-10-21 Pressure Calibration Variation on these units
    - they all need to be multipled by 3 as they have a non-standard 30Bar sensor on them
    - if this happens in future, update code for variable sensors
2023-03-03 Update 03_PopUpFloat_Translater.ipynb
    correct temperature version code

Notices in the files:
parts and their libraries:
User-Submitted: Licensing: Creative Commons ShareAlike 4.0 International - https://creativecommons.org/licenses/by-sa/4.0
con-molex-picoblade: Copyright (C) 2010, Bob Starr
